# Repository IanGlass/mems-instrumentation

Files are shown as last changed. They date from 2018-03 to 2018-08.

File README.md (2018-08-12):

# MEMS-Instrumentation
16 channel instrumentation circuit designed with emphasis on high precision, low-noise sampling of low sensitivity MEMS sensors in Wheatstone bridge configuration. The circuit does not digitize results and requires an external ADC, such as the NI 6009 DAQ.

## Specifications
* CMRR: 124 dB
* Input Voltage Range: 4.5 V to 5.5 V
* Gain: 1x, 10x, 100x, or 1,000x
* Channels: 16
* Sensor Drive Voltage: +- 1.25 V

## Single Channel

The circuit needs an external DAQ to quantize samples and has two gain select digital lines designated 'A0' and 'A1' to select 1x, 10x, 100x or 1000x, refer to the PGA204 doc for bit patterns. Anti-aliasing is implemented for signals below 500 Hz and needs to be changed for higher sample rates. Each channel contains a 4x1 header to accommodate a 'stub tester' for differential sensing.

<p align="center">
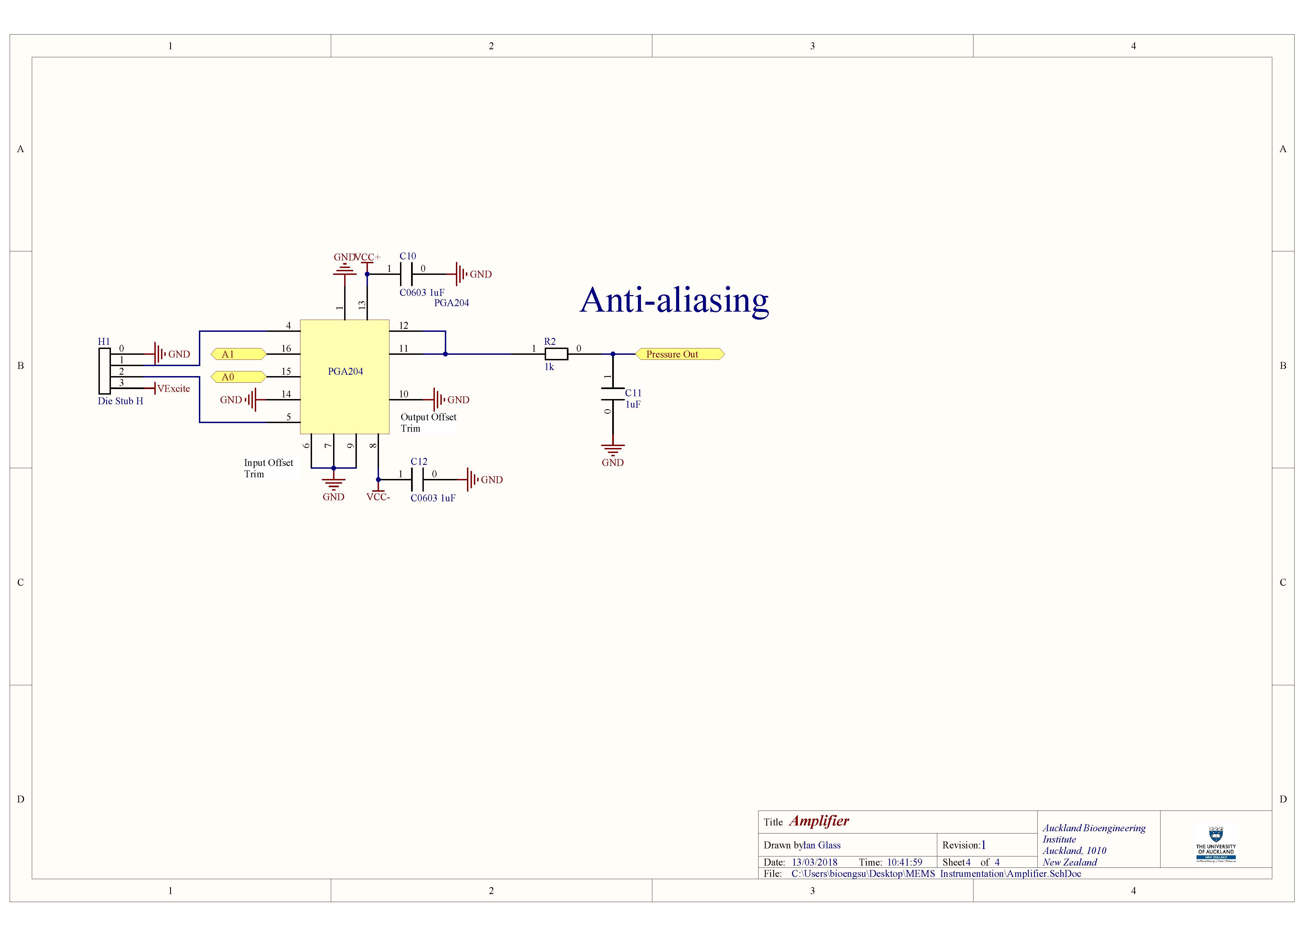
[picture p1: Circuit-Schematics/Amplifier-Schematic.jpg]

</p>

## Stub Tester

The sensor is mounted in a 'stub tester' and need to be balanced with surface mount resistors. Each sensor element is configured in a voltage divider topology to create a Wheatstone bridge. 'Balancing' means to add resistors such that the two out voltage divider voltages are equal and the differential voltage is zero. This is done to give the largest measurement range through the operational amplifier, as the output will saturate close to VCC.

<p align="center">
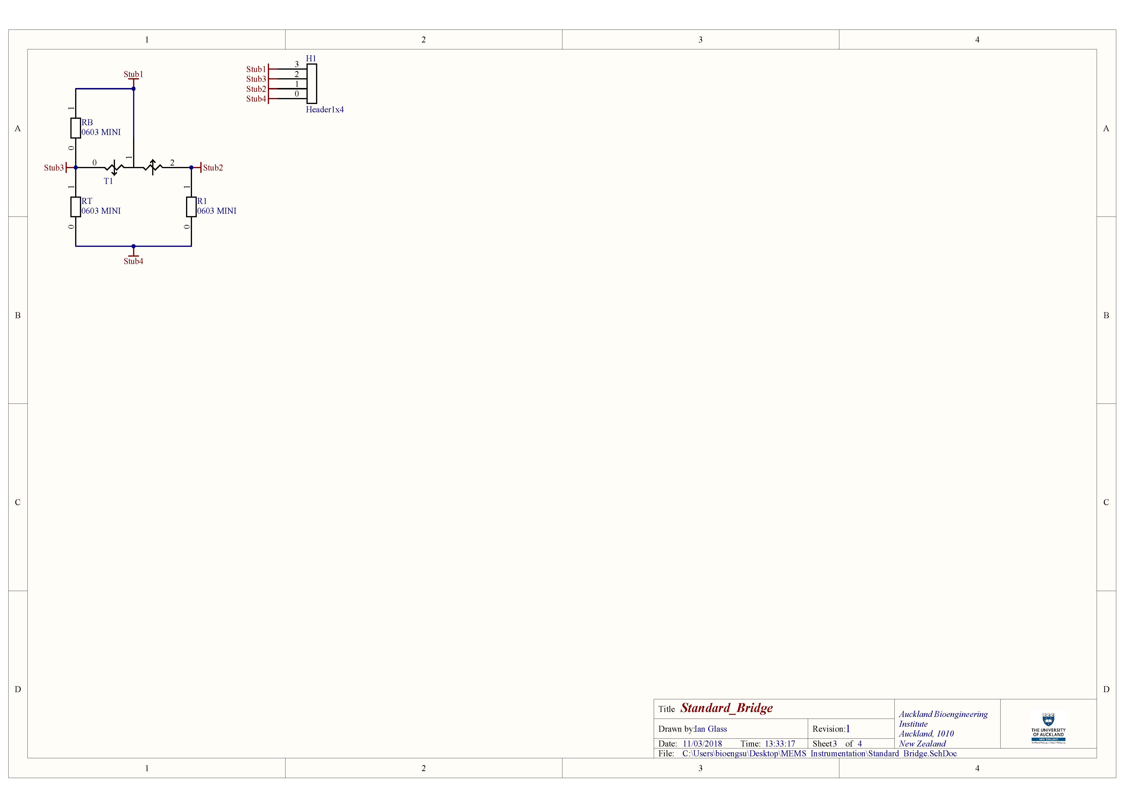
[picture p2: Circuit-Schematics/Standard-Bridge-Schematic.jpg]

</p>

## Complete Circuit

The circuit has 16 PGA204 amplifier channels and can handle 16 sensors concurrently.  On-board V regulators supply +- 1.25 V and are switched with 'Cont1' and 'Cont2' for +ve and -ve supply voltages respectively. This means sensor supply voltage can be modulated if needed. Boards are 6-layered with internal GND, VCC+, VCC- and VExcite power and ground planes. The voltage regulators can be replaced to provide a higher drive voltages as required.

<p align="center">
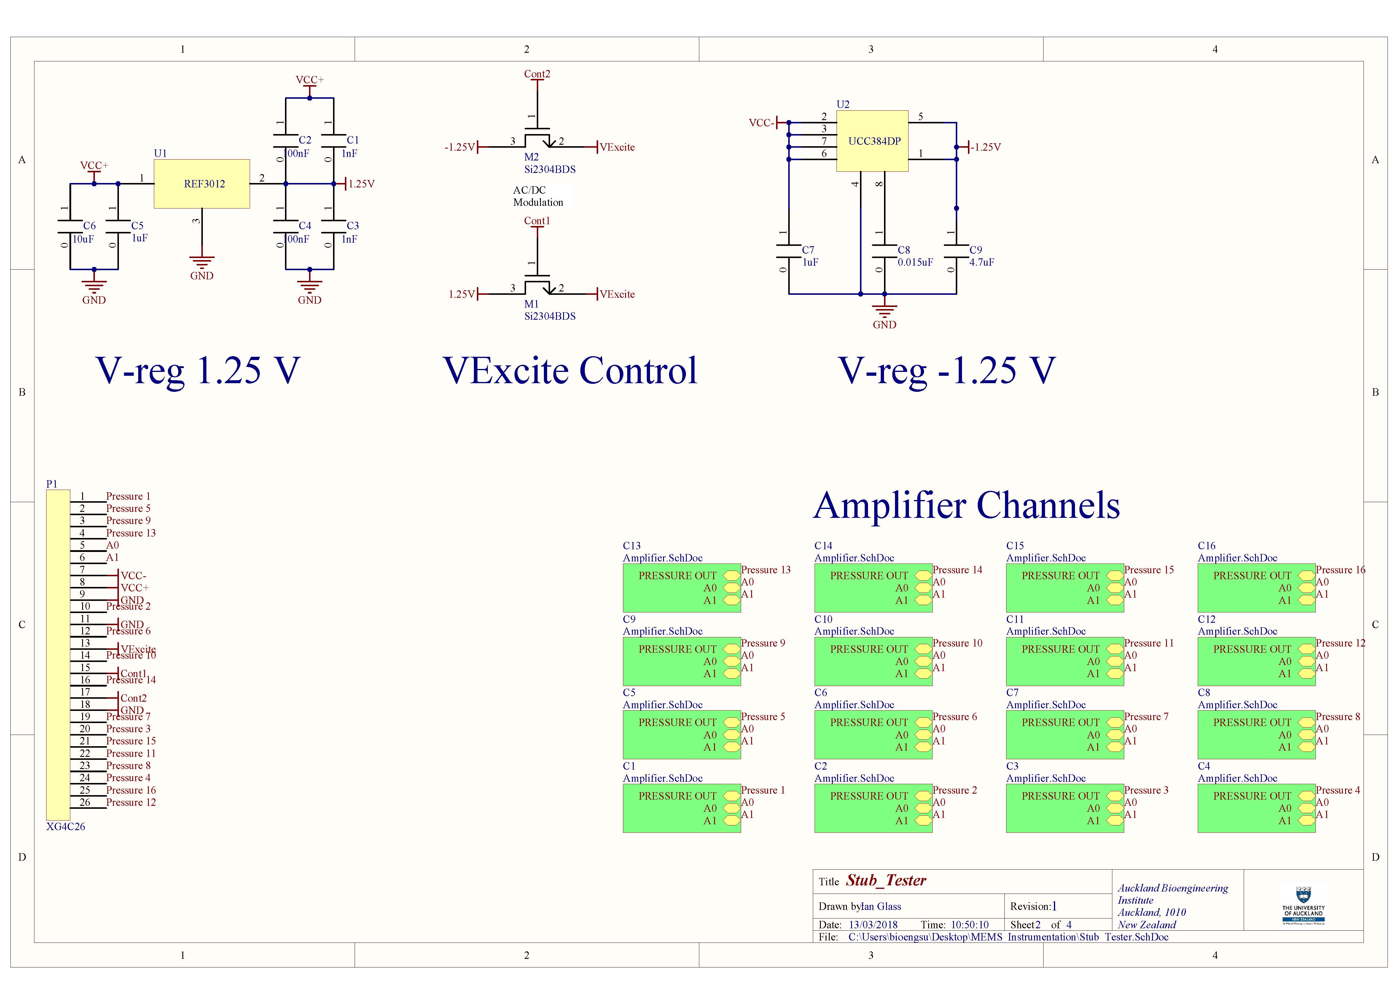
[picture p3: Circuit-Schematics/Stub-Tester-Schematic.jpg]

</p>

PCB overview showing the 16 channels, a designated area for power regulation ICs, a footprint for the 26 pin ribbon cable header and a single 'stub tester' PCB. 
<p align="center">
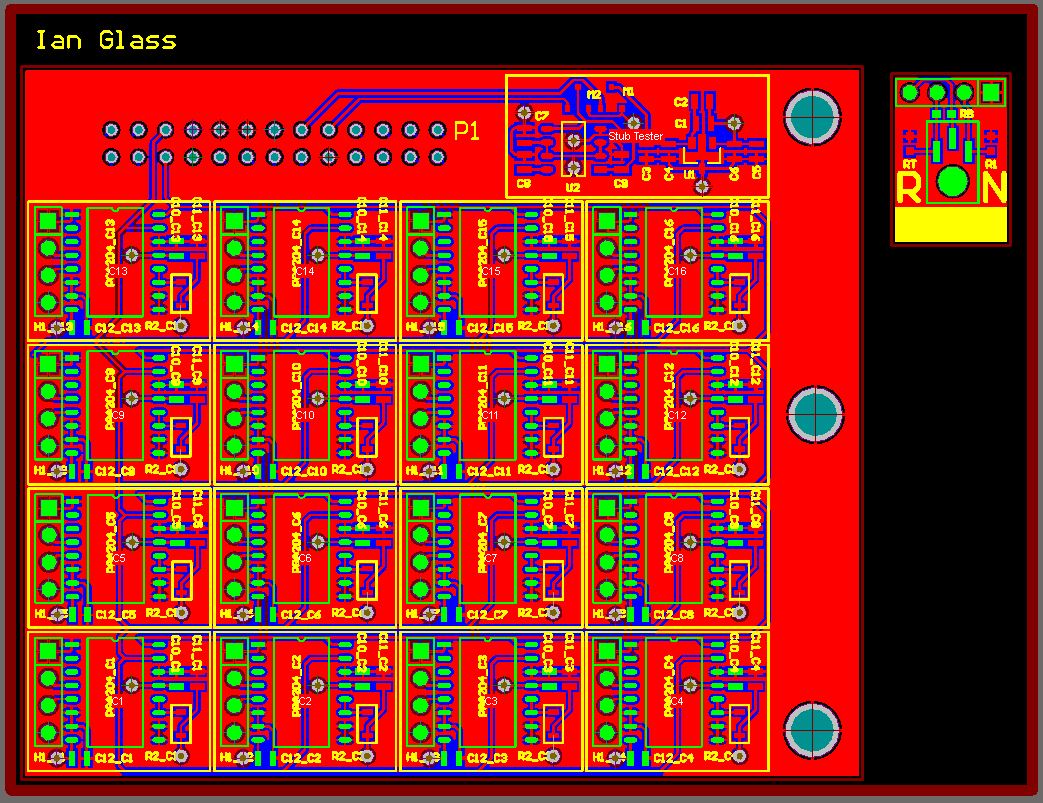
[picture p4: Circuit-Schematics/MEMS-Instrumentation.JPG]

</p>

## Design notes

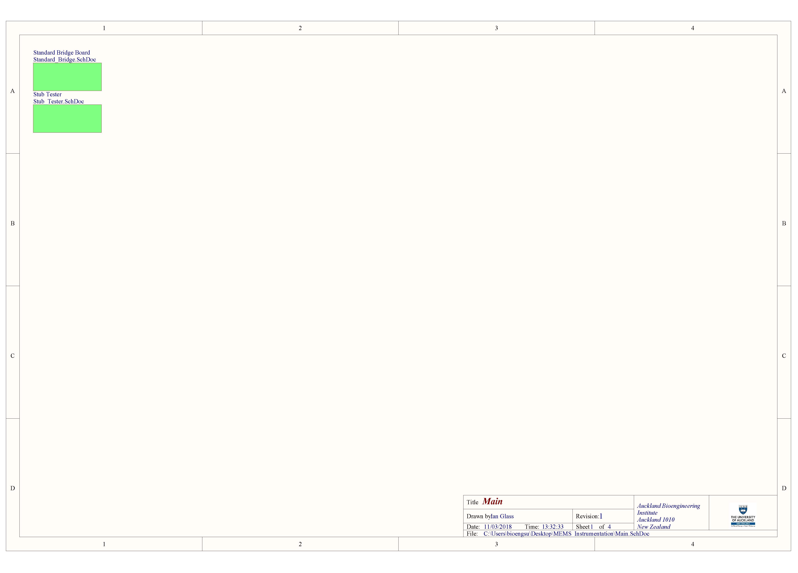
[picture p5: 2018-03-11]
Circuit-Schematics/Main-Schematic.jpg

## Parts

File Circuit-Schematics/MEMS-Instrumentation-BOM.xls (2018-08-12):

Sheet: Instructions
Instructions to Requesters :
1 | Check the Preferred/Recommended Supplier list and look for a Supplier.
2 | If products can only be sourced from an external supplier who is neither a preferred nor recommended supplier, please check if it accepts credit cards.
3 | If the external supplier does not have credit card facility, it needs to be set up in the system for ordering.
4 | To set up a new supplier, please provide the following:
 | a | Justification as to why the existing suppliers cannot be used (one paragraph will do)
 | b | Local Supplier : Company ID
 | c | Local Supplier : Bank account details in the form of a deposit slip or bank statement as per auditor's requirements
 | d | Foreign Supplier : An email with the Supplier's bank account details will do
 | e | Indicate the frequency of ordering (e.g., one-off, 3 times a year etc.)
5 | Get a written and official quotation from the Supplier. This is particularly important for big value or overseas orders, as they have the terms and conditions on delivery, payment terms, exchange rates
 | and freights on them which we need to be aware of.
6 | Fill out the ABI Purchase Requisition Form (please always include the freight costs in the Requisition Form).
7 | Obtain approval from the relative PI/Supervisor (email approval is accepted).
8 | Email the completed Purchase Order Form (together with the Quotation) to the Purchasing Team (bioeng-ordering-bounces@list.bioeng.auckland.ac.nz) and cc the relative Supervisor/PI.
9 | Please ensure all purchasing requests must go through the Purchasing Team (incl. all local and overseas requests). Buy first and get reimbursed is not recommended.
 | Note: Overseas requests refer to requests from staff/students who are overseas for a field visits and need to make consumable purchases and deliver to an overseas address.
 | Such requests can still be emailed to the Purchasing Team for processing as normal.
10 | Please quote the REF NO. whenever you make enquiries to the Purchasing Team

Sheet: Req Form
ABI PURCHASE ORDER REQUISITION FORM
SECTION A | Requester |  |  |  | Ref No
Requester Name | Ian Glass |  |  |  | Date | 2014-10-27
Email | igla626@aucklanduni.ac.nz |  |  |  | Ext
Approver's Name | David Budgett
Location | Level 6 | Please select
SECTION B | Vendor
Vendor Name | Digikey |  |  |  | Phone
Contact Person |  |  |  |  | Fax
Vendor Address
Email Address
Quotation No
Delivery Address
Other Del Address
Expected Delivery Date
SECTION C | Goods and Services
Item code | Description | Qty | Unit | Unit Price | Currency | Discount | Total Amount
PGA204BU | Op Amp | 16 |  | 24.9668 |  |  | $399.47
C0603C105M3PACTU | Cap 0603 1uF | 200 |  | 0.0643 |  |  | $12.86
PPTC041LFBN-RC | Die Header | 16 |  | 0.5316 |  |  | $8.51
RC0603FR-071KL | Res 0603 1k | 16 |  | 0.02 |  |  | $0.32
C0603C106M9PACTU | Cap 0603 10uF | 5 |  | 0.51 |  |  | $2.55
C0603C104Z3VACTU | Cap 0603 100nF | 8 |  | 0.14 |  |  | $1.12
C0603C102J5GACTU | Cap 0603 1nF | 8 |  | 0.14 |  |  | $1.12
C0603C153K5RACTU | Cap 0603 0.015uF | 5 |  | 0.14 |  |  | $0.70
C0603C475K9PACTU | Cap 0603 4.7uF | 5 |  | 0.18 |  |  | $0.90
REF3012TB-GT3 | V Regulator | 4 |  |  |  |  | $0.00
UCC384DP-ADJ | V Regulator | 4 |  | 8.33 |  |  | $33.32
XG4C-2634 | XG4C26 | 4 |  | 1.94 |  |  | $7.76
SI2304BDS-T1-GE3 | N MOSFET | 13 |  | 0.515 |  |  | $6.70
AWG28-26/F/300 | 26 wire ribbon cable (7.62m) | 1 |  | 58.89 |  |  | $58.89
4626-6000 | 26 pin header plug male | 4 |  | 9.78 |  |  | $39.12
SFH210-PPPC-D13-ID-BK | 26 pin Header plug female | 8 |  | 1.54 |  |  | $12.32
 |  |  |  |  | Sub Total |  | $534.21
 |  |  |  |  | Freight |  | $5.00
 |  |  |  |  | Total |  | $539.21
 |  |  | Please Select/Type Y/N |  | GST | Y | $80.88
 |  |  |  |  | Total incl GST |  | $620.09
SECTION D | Funding and Coding
Category Code | CON - Consumables | Please select
Accepts Credit Card |  | Please select
Activity Centre |  | Please select
Project ID |  | Please enter the project ID except for 9677 and 1750
Project Name |  | Please type the Project name
NB: Please send the completed form together with the quotation to the Purchasing Team (bioeng-ordering@list.bioeng.auckland.ac.nz) and cc the relative supervisor/PI
 | Level 4
 | Level 5
 | Level 6
 | Level 7
 | Level 8
 | Physiology
Assets | CAP - Assets
Catering | CAT - Catering
Conference | CNF - Conference
Consumables | CON - Consumables
General | GEN - General
Travel | TRA - Travel
Workshop | WKS - Workshop
GST/Import Fee | GEN - GST/Import Fee
Renovation | REN - Renovation
Subscription | SUB - Subscription
Software | SFW - Software
Attractive Assets | ATT - Attractive Assets
 | Auckland Bioengineering Institute, Level 6, UniServices House, 70 Symonds Street, Auckland
 | Physiology via Loading Dock, FMHS, Corner Park Rd & Park Ave, Grafton, Auckland. Attn: Dane Gerneke, Mob: 021 045 8867
 | If delivery address is not listed, please enter it below

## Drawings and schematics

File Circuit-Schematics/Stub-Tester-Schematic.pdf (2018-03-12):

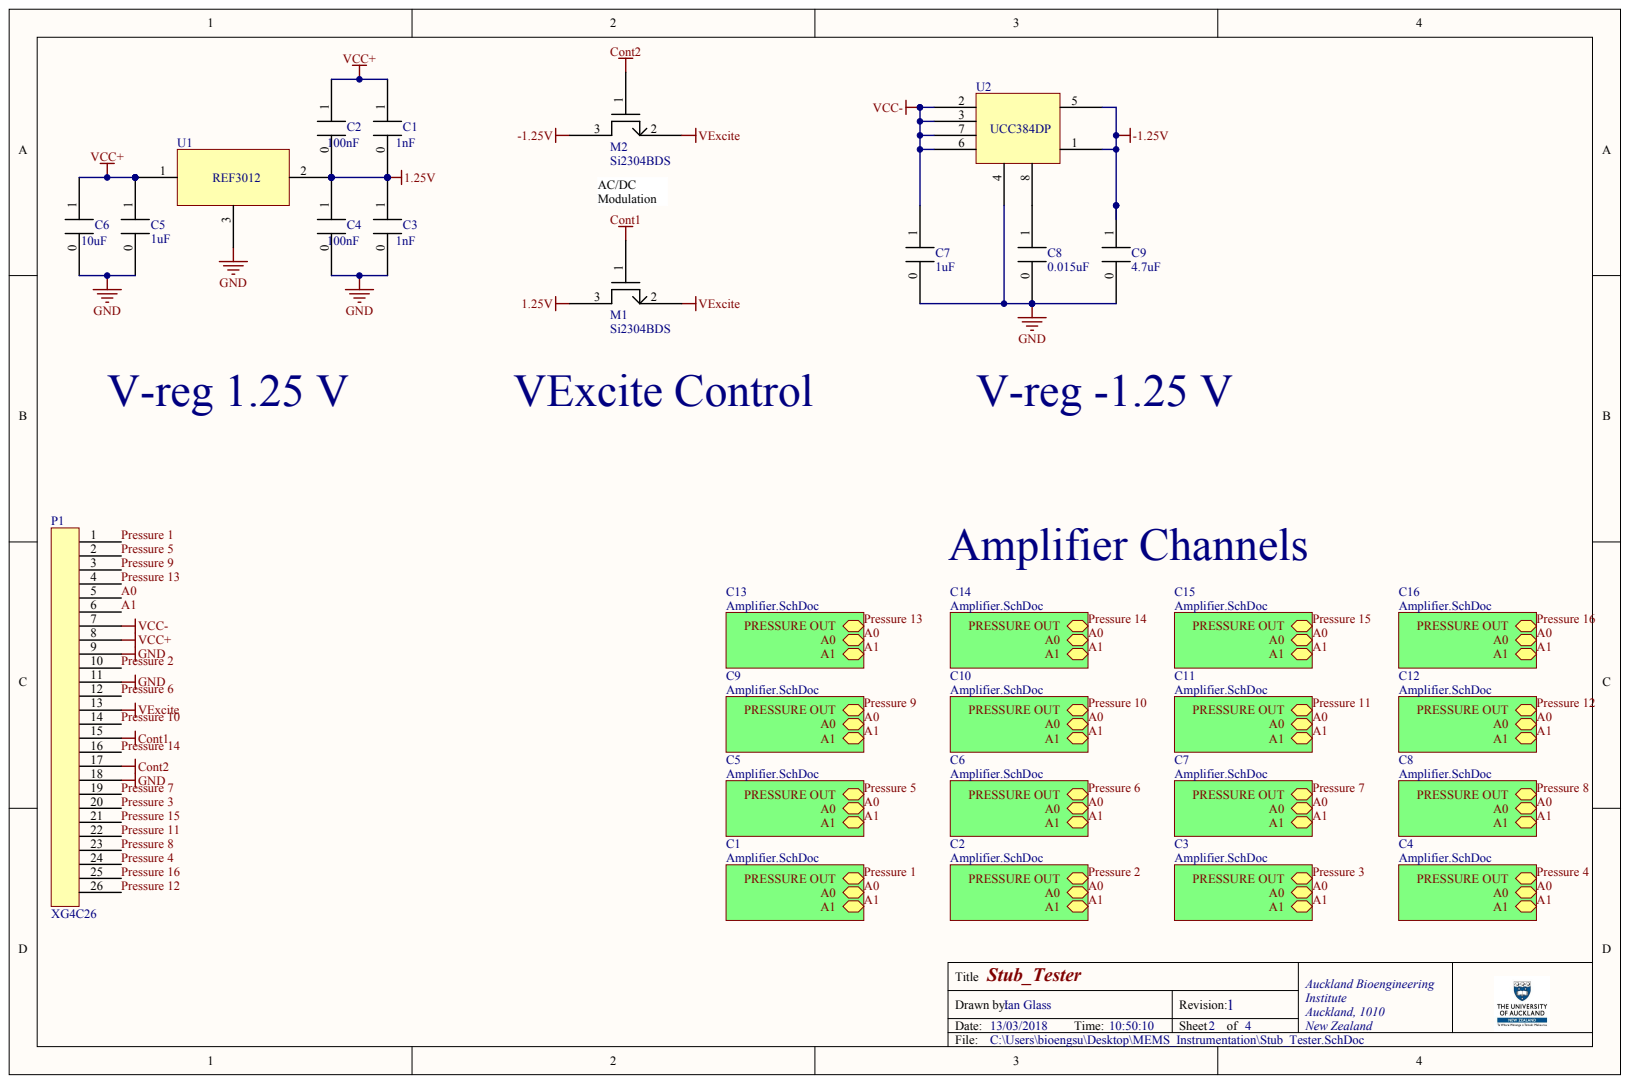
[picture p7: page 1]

Stub_Tester Title | Auckland Bioengineering Institute Auckland, 1010 New Zealand

Drawn by: Ian Glass | Revision: 1

Date: 13/03/2018 Time: 10:50:10 | Sheet 2 of 4

C:\Users\bioengsu\Desktop\MEMS_Instrumentation\Stub_Tester.SchDoc

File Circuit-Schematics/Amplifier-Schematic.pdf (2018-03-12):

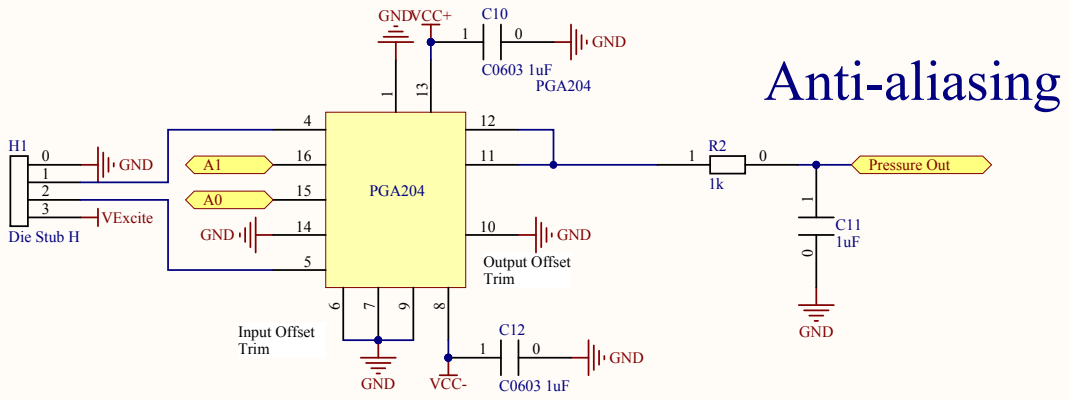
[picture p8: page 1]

Amplifier Title | Auckland Bioengineering Institute Auckland, 1010 New Zealand

Drawn by: Ian Glass | Revision: 1

Date: 13/03/2018 Time: 10:41:59 | Sheet 4 of 4

C:\Users\bioengsu\Desktop\MEMS_Instrumentation\Amplifier.SchDoc

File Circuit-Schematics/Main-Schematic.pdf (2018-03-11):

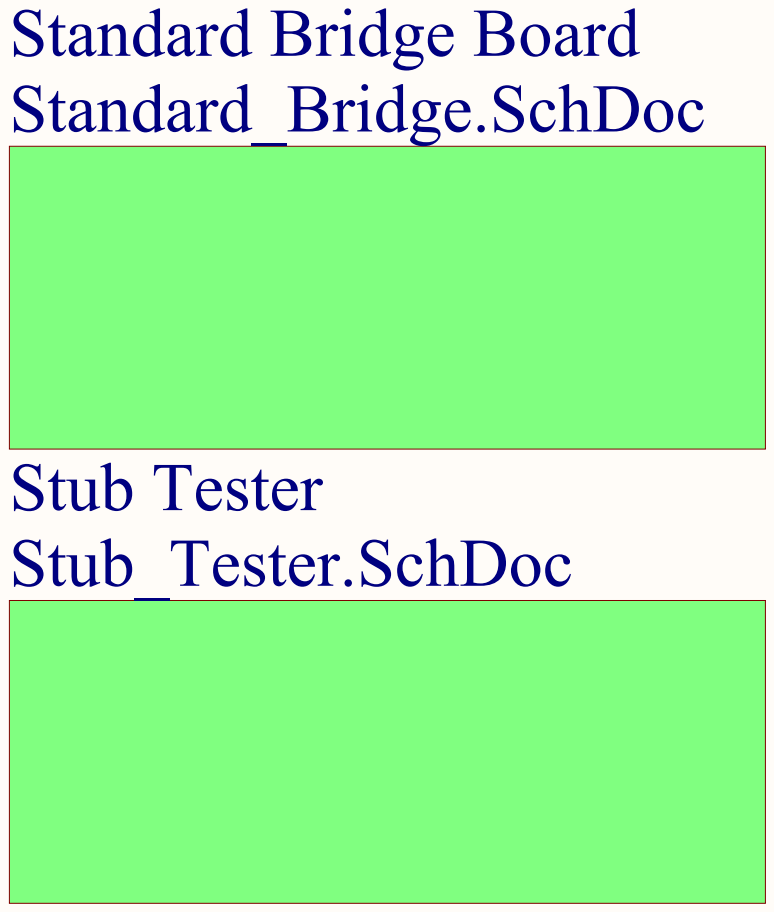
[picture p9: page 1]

Main Title | Auckland Bioengineering Institute Auckland 1010 New Zealand

Drawn by: Ian Glass | Revision: 1

Date: 11/03/2018 Time: 13:32:33 | Sheet 1 of 4

C:\Users\bioengsu\Desktop\MEMS_Instrumentation\Main.SchDoc

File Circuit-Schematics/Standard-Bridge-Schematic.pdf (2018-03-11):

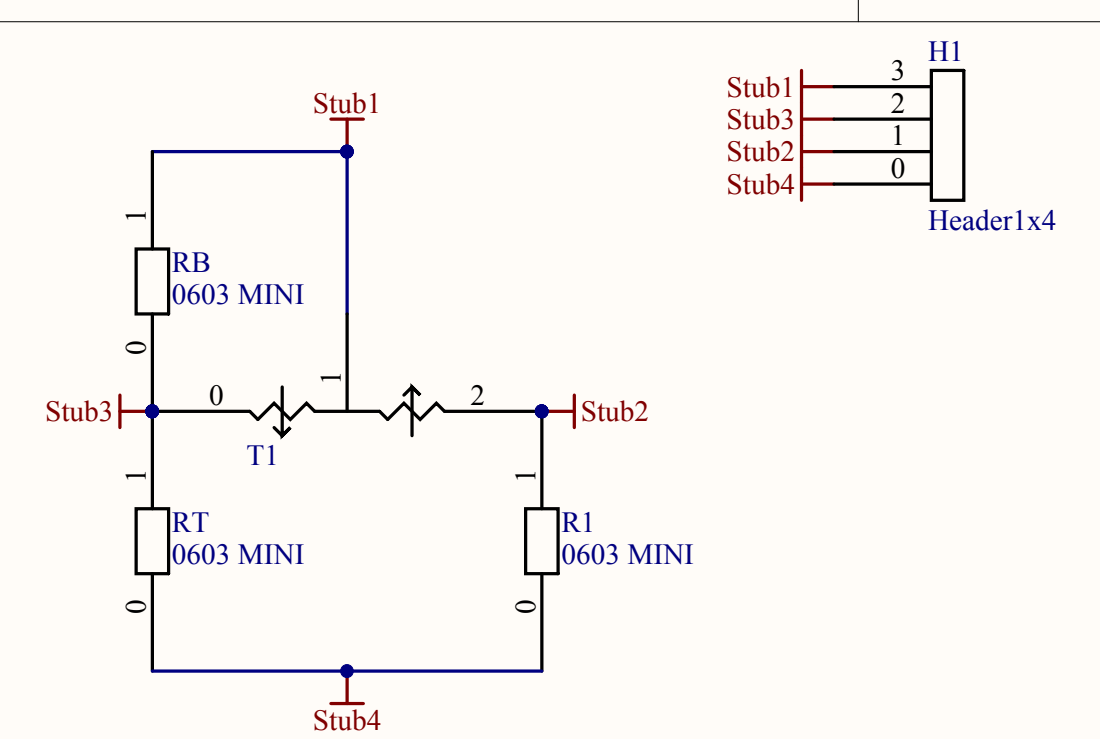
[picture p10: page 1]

Standard_Bridge Title | Auckland Bioengineering Institute Auckland, 1010 New Zealand

Drawn by: Ian Glass | Revision: 1

Date: 11/03/2018 Time: 13:33:17 | Sheet 3 of 4

C:\Users\bioengsu\Desktop\MEMS_Instrumentation\Standard_Bridge.SchDoc

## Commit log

2018-08-12 Update to readme
    [MEMS-Instrumentation-BOM.xls]
2018-08-12 Updated File Structure
    [Amplifier.SchDoc, MEMS-Instrumentation-BOM.xls, MEMS_Instrumentation.PcbDoc, MEMS_Instrumentation.PrjPCB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]
